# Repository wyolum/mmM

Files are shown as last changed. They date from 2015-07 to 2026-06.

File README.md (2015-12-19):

# mmMercury
mmMercury is an Open Hardware, blood pressure measurement device (not FDA approved).
=======

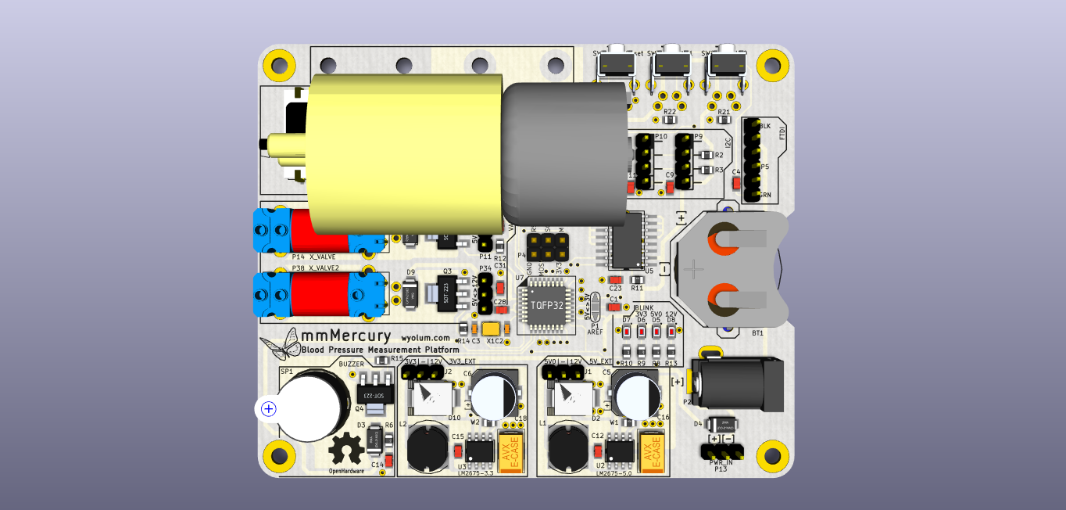
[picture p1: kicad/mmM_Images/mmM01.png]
mmMercury top


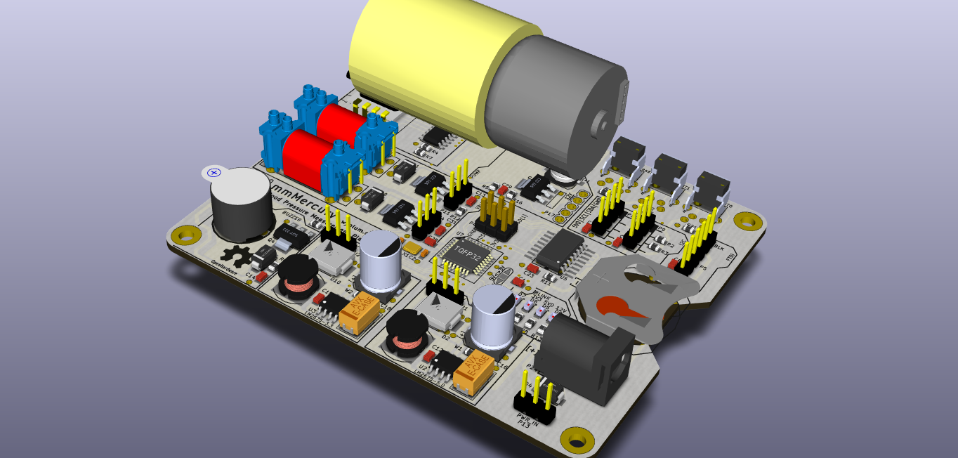
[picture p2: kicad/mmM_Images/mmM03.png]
mmMercury ortho


License
-------
[CERN Open Hardware Licence v1.2 ]

[CERN Open Hardware Licence v1.2 ]:http://www.ohwr.org/attachments/2388/cern_ohl_v_1_2.txt

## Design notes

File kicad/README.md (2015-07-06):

# uCm
uCmini is a laboratory, Open Hardware, blood pressure measurement device (not FDA approved).
Along with the hardware, we will develop an Android app to do the compute BP from the streaming raw data from uCm.  The app will store your BP history, and plot the history. The desire is to get the Open communities involved in the the algorithm development. If we use the Bluefruit Ez-link, the same hardware will work with an FTDI cable.

License
-------
[CERN Open Hardware Licence v1.2 ]

[CERN Open Hardware Licence v1.2 ]:http://www.ohwr.org/attachments/2388/cern_ohl_v_1_2.txt

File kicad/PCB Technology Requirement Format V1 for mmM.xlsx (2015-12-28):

深圳矽递科技有限公司Seeed Technology Inc.
PCB Technology Requirement Format
PCB Name & Version | mmMercury, rev 1
PCB Material PCB板材： | (Rigid)FR－4
PCB Size PCB大小： | mm | ( 99 ) × ( 80 )
PCB Layer PCB层数： | 2
Thickness PCB厚度：
 |  | 1.6mm
Copper Weight铜厚： | 1oz
PCB Colour阻焊颜色： |  | White白色
Silkscreen字符颜色： |  | Black黑色
Pads Finished焊盘喷镀： | (Hasl-lead free)无铅喷锡
Via solder mask阻焊覆盖： |  | solder mask opening过孔开窗
Minimum trace/space (mm)最小线宽 | 0.178mm | Minimum hole size (mm)最小孔径 | 0.508mm
Special requirements特殊工艺： | No | (Put requirements here)
Comment:

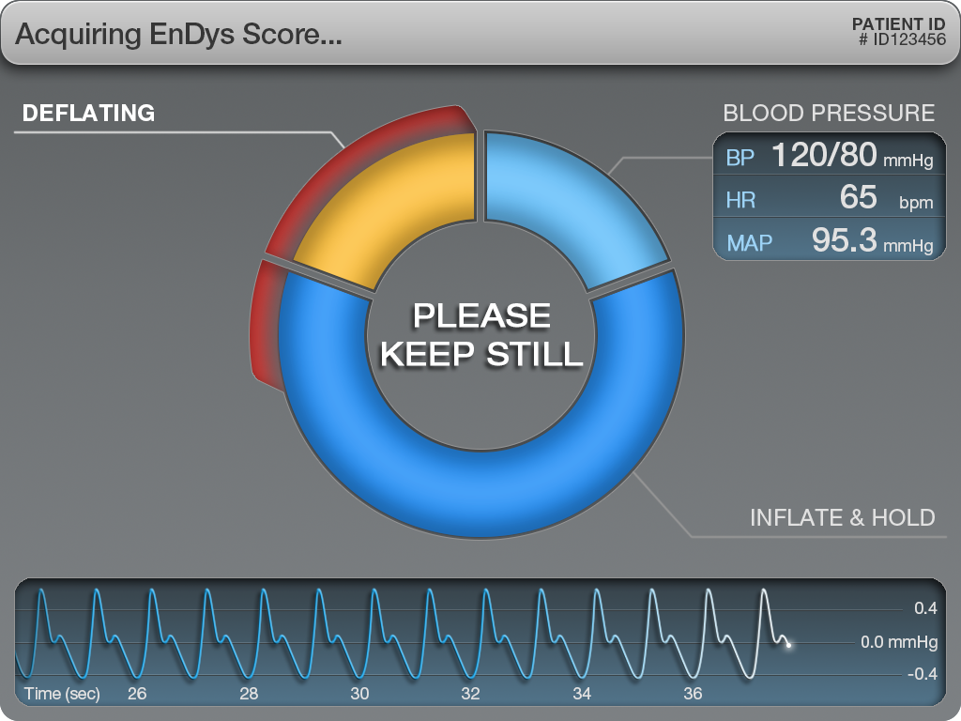
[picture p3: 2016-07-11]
scripts/control_panel/images/4_deflating complete.png

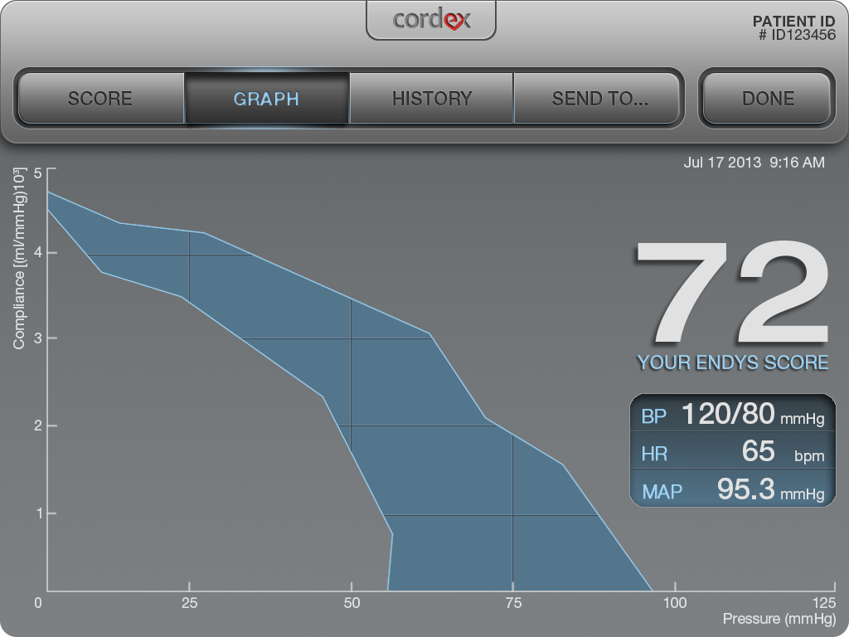
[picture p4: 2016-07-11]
scripts/control_panel/images/6_graph.png

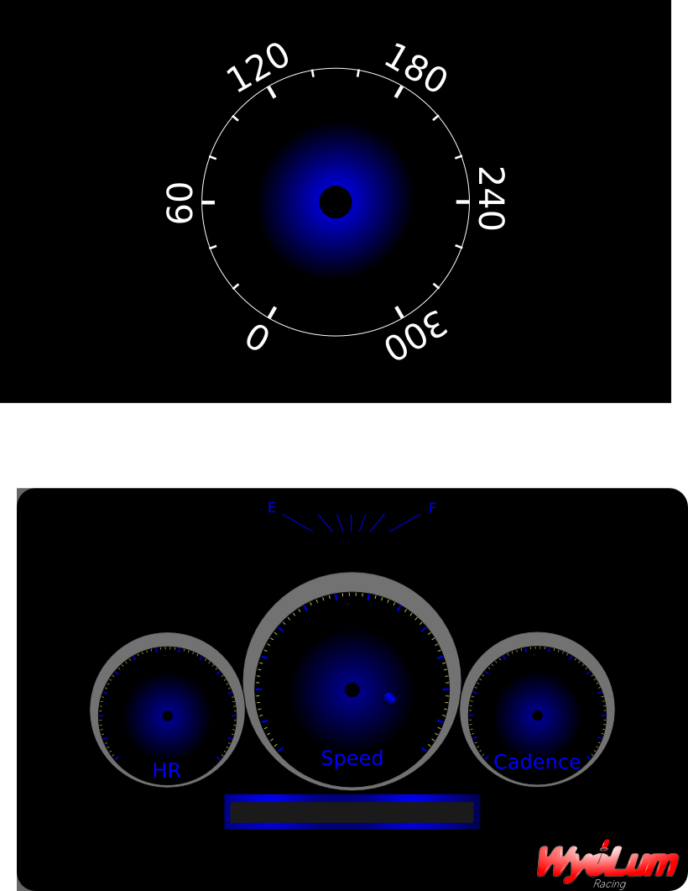
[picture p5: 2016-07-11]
scripts/control_panel/images/background.png

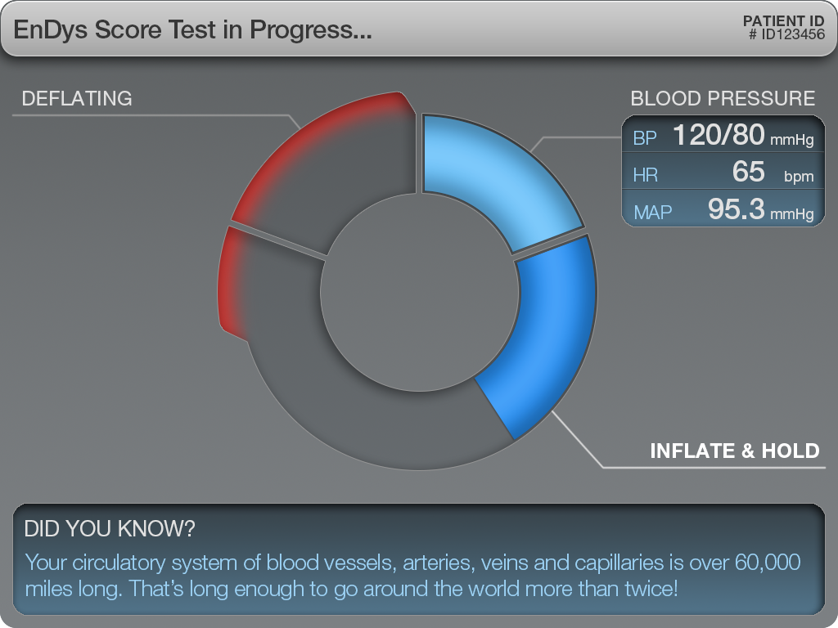
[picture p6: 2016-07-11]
scripts/control_panel/images/2_inflate&hold.png

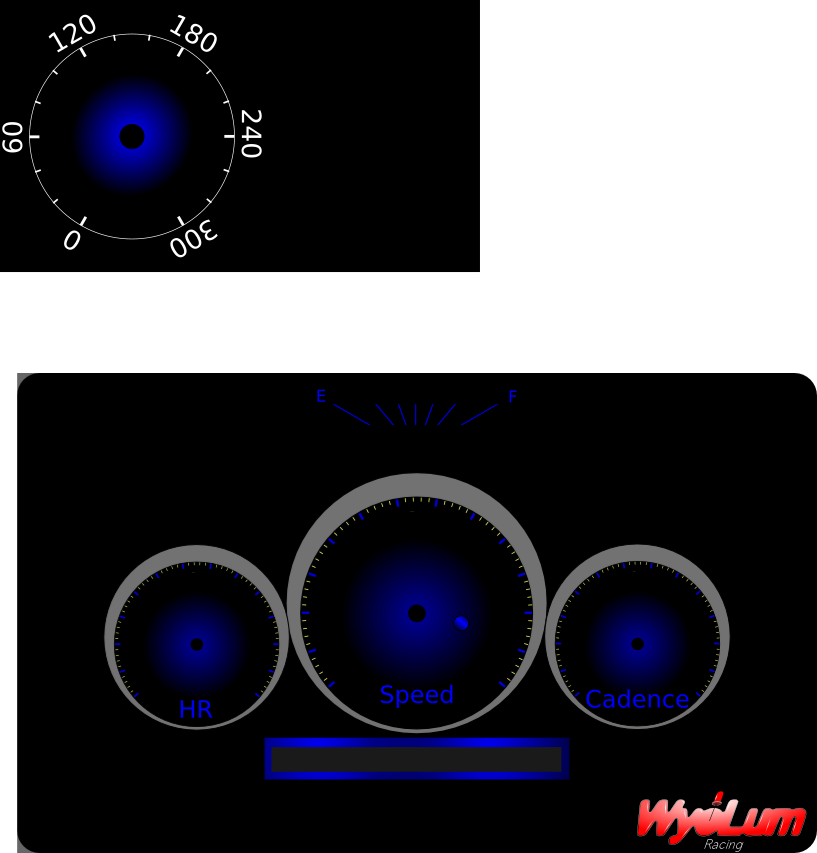
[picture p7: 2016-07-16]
scripts/control_panel/images/background_480_272.png

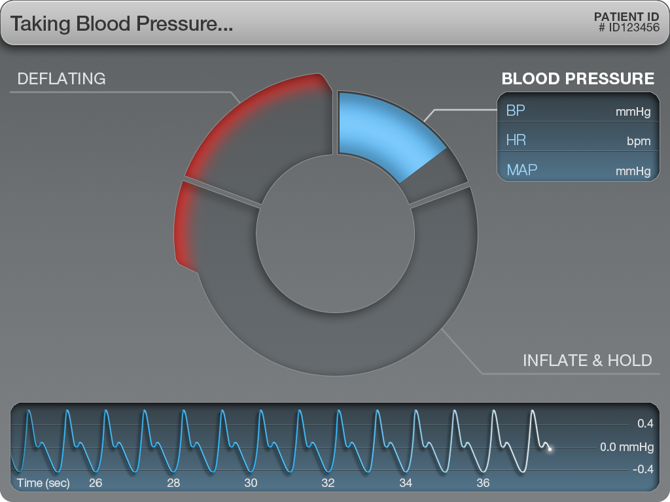
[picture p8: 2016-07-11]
scripts/control_panel/images/1_blood pressure.png

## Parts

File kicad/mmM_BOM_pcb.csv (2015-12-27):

Id | Designator | Package | Quantity | Designation | Supplier and ref
1 | REF62,REF61,REF60,REF1,REF2,REF3,REF4,REF5,REF6,REF7,REF8,REF9,REF10,REF11,REF12,REF13,REF14,REF15,REF16,REF17,REF18,REF19,REF20,REF21,REF22,REF23,REF24,REF25,REF26,REF27,REF55,REF56,REF57,REF58 | via01 | 34 | via01
2 | REF59,REF28,REF29,REF30,REF31,REF32,REF33,REF34,REF35,REF36,REF37,REF38,REF39,REF40,REF41,REF42,REF43,REF44,REF45,REF46,REF47,REF48,REF49,REF50,REF51,REF52,REF53,REF54 | via_th | 28 | via01
3 | B7,B9 | I_O | 2 | PC1
4 | B1,B2,B3 | I_O | 3 | I_O
5 | B4,B12 | I_O | 2 | PB0
6 | B8 | I_O | 1 | PC0
7 | B10 | I_O | 1 | PC6
8 | B11 | I_O | 1 | PC7
9 | BT1 | CR2032 | 1 | BATT_HOLDER
10 | D1,D3,D4,D9 | diode-DO214AC | 4 | ES1D-13-F
11 | D5 | led_0805 | 1 | 5V0
12 | D6 | led_0805 | 1 | 3V3
13 | D7 | led_0805 | 1 | BLINK
14 | D8 | led_0805 | 1 | 12V
15 | P1 | ShortLink2 | 1 | AREF
16 | P4 | Header_ISP | 1 | ICSP
17 | P5 | Header_FTDI | 1 | FTDI
18 | P9,P10 | pin_strip_4-90 | 2 | C3SB
19 | P11 | Header_3 | 1 | VSel_Vlv
20 | P13 | Header_2 | 1 | PWR_IN
21 | P14 | X_Valve_2 | 1 | X_VALVE
22 | P24 | JACK_ALIM | 1 | PWR_IN
23 | P34 | Header_3 | 1 | VSel_Vlv2
24 | P38 | X_Valve_2 | 1 | X_VALVE2
25 | Q1,Q2,Q3,Q4 | SOT223 | 4 | BCP5416TA
26 | SC6,SC7,SC9,SC10 | vite_3mm | 4 | SCREW
27 | SP1 | Speaker | 1 | BUZZER
28 | SW1 | SW_PB_V_H | 1 | Reset
29 | SW2 | SW_PB_V_H | 1 | INT0
30 | SW3 | SW_PB_V_H | 1 | INT1
31 | U5 | DS3231 | 1 | DS3231N
32 | U7 | TQFP32 | 1 | ATMEGA328P-AU-ND
33 | X1 | Xtal_SMD3 | 1 | 16MHz
34 | G1,G2 | Logo-WL3 | 2 | Logo_Wyolum
35 | G3,G4 | OSHW_6mm | 2 | Logo_OH
36 | R22,R21,R11,R4,R3,R2,R1,R12,R14,R15,R16 | r_0805 | 11 | 10k
37 | R13,R10,R6 | r_0805 | 3 | 1k
38 | R9 | r_0805 | 1 | 120E
39 | R8 | r_0805 | 1 | 330E
40 | R5 | r_0805 | 1 | 4k7
41 | C3,C2 | c_0603 | 2 | 22pF
42 | P17 | Pump_P54E01R_03 | 1 | PUMP
43 | W1,W2 | r_0805 | 2 | EN
44 | U3 | SO8E | 1 | LM2675-3.3
45 | U2 | SO8E | 1 | LM2675-5.0
46 | C15,C12 | c_0805 | 2 | 10nF
47 | C1,C4,C7,C8,C9,C10,C11,C13,C14,C17,C23,C28,C29,C31,C19 | c_0805 | 15 | 100nF
48 | C18,C16 | C_2917_HandSoldering | 2 | 100uF 10V
49 | J1 | Header_3 | 1 | 5V_EXT
50 | J2 | Header_3 | 1 | 3V3_EXT
51 | C6,C5 | C_ELCO_SMD_8x10 | 2 | 330uF 25V
52 | L2,L1 | Choke_SMD_Wuerth-784775133 | 2 | 33uH
53 | R7 | r_0805 | 1 | Zero
54 | U1 | TXB0104D | 1 | TXB0104D
55 | D10,D2 | DO-214AB | 2 | SS35
56 | C27 | C_ELCO_SMD | 1 | 100uF
57 | P7 | HCEM500GUH9P3 | 1 | GAGE_PR

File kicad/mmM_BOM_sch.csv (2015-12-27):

Reference | Value | Footprint | Datasheet | manf#
P4 | ICSP | mmM:Header_ISP |  | PREC003DAAN-RC
P1 | AREF | mmM:ShortLink2
SW1 | Reset | mmM:SW_PB_V_H |  | FSMRA3JH
X1 | 16MHz | mmM:Xtal_SMD3 |  | TSX-3225 16.0000MF09Z-AC3
R3 | 10k | mmM:r_0805 |  | RMCF0805JT10K0
R2 | 10k | mmM:r_0805 |  | RMCF0805JT10K0
R1 | 10k | mmM:r_0805 |  | RMCF0805JT10K0
C3 | 22pF | mmM:c_0603 |  | CL10C220JB8NNNC
C2 | 22pF | mmM:c_0603 |  | CL10C220JB8NNNC
P5 | FTDI | mmM:Header_FTDI |  | PREC006SAAN-RC
U7 | ATMEGA328P-AU-ND | mmM:TQFP32 |  | ATMEGA328-AU
B8 | PC0 | mmM:I_O
B9 | PC1 | mmM:I_O
B10 | PC6 | mmM:I_O
B11 | PC7 | mmM:I_O
B12 | PB0 | mmM:I_O
SW2 | INT0 | mmM:SW_PB_V_H |  | FSMRA3JH
SW3 | INT1 | mmM:SW_PB_V_H |  | FSMRA3JH
R22 | 10k | mmM:r_0805 |  | RMCF0805JT10K0
R21 | 10k | mmM:r_0805 |  | RMCF0805JT10K0
C28 | 100nF | mmM:c_0805 |  | CL21B104KCC5PNC
B4 | PB0 | mmM:I_O
SC6 | SCREW | mmM:vite_3mm
SC9 | SCREW | mmM:vite_3mm
SC7 | SCREW | mmM:vite_3mm
SC10 | SCREW | mmM:vite_3mm
B7 | PC1 | mmM:I_O
C1 | 100nF | mmM:c_0805 |  | CL21B104KCC5PNC
C4 | 100nF | mmM:c_0805 |  | CL21B104KCC5PNC
C19 | 100nF | mmM:c_0805 |  | CL21B104KCC5PNC
M1 | OSHW-LOGO | OSHW-LOGO
C27 | 100uF | mmM:C_ELCO_SMD_6x8 |  | UWT1V101MCL1GS
P9 | C3SB | mmM:pin_strip_4-90 |  | PREC004SAAN-RC
U1 | TXB0104D | mmM:TXB0104D |  | TXB0104DR
R4 | 10k | mmM:r_0805 |  | RMCF0805JT10K0
Q1 | BCP5416TA | mmM:SOT223 |  | BCP5416TA
P14 | X_VALVE | mmM:X_Valve_2 |  | X-1-05-S-F
P7 | GAGE_PR | mmM:HCEM500GUH9P3 |  | HCEM500GUH9P3
D1 | ES1D-13-F | mmM:Diode-SMA |  | ES1D-13-F
C17 | 100nF | mmM:c_0805 |  | CL21B104KCC5PNC
C13 | 100nF | mmM:c_0805 |  | CL21B104KCC5PNC
C11 | 100nF | mmM:c_0805 |  | CL21B104KCC5PNC
C10 | 100nF | mmM:c_0805 |  | CL21B104KCC5PNC
C9 | 100nF | mmM:c_0805 |  | CL21B104KCC5PNC
C8 | 100nF | mmM:c_0805 |  | CL21B104KCC5PNC
C7 | 100nF | mmM:c_0805 |  | CL21B104KCC5PNC
P10 | C3SB | mmM:pin_strip_4-90 |  | PREC004SAAN-RC
P11 | VSel_Vlv | mmM:Header_3 |  | PREC003SAAN-RC
Q2 | BCP5416TA | mmM:SOT223 |  | BCP5416TA
P18 | Pump_Cable
R5 | 4k7 | mmM:r_0805 |  | RMCF0805JT4K70
C29 | 100nF | mmM:c_0805 |  | CL21B104KCC5PNC
Q3 | BCP5416TA | mmM:SOT223 |  | BCP5416TA
P38 | X_VALVE2 | mmM:X_Valve_2 |  | X-1-05-S-F
D9 | ES1D-13-F | mmM:Diode-SMA |  | ES1D-13-F
C31 | 100nF | mmM:c_0805 |  | CL21B104KCC5PNC
P34 | VSel_Vlv2 | mmM:Header_3 |  | PREC003SAAN-RC
C14 | 100nF | mmM:c_0805 |  | CL21B104KCC5PNC
Q4 | BCP5416TA | mmM:SOT223 |  | BCP5416TA
D3 | ES1D-13-F | mmM:Diode-SMA |  | ES1D-13-F
R6 | 1k | mmM:r_0805 |  | RMCF0805JT1K00
SP1 | BUZZER | mmM:Speaker |  | PS1240P02BT
P17 | PUMP | mmM:Pump_P54E01R_02 |  | P54E01R
R7 | Zero | mmM:r_0805 |  | RMCF0805ZT0R00
R16 | 10k | mmM:r_0805 |  | RMCF0805JT10K0
R15 | 10k | mmM:r_0805 |  | RMCF0805JT10K0
R12 | 10k | mmM:r_0805 |  | RMCF0805JT10K0
R14 | 10k | mmM:r_0805 |  | RMCF0805JT10K0
R10 | 1k | mmM:r_0805 |  | RMCF0805JT1K00
R13 | 1k | mmM:r_0805 |  | RMCF0805JT1K00
R9 | 120E | mmM:r_0805 |  | RMCF0805JT120R
R8 | 330E | mmM:r_0805 |  | RMCF0805JT330R
P24 | PWR_IN | mmM:JACK_ALIM |  | PJ-002B
D7 | BLINK | mmM:led_0805 |  | LG M67K-H1J2-24-Z
D8 | 12V | mmM:led_0805 |  | LG M67K-H1J2-24-Z
D6 | 3V3 | mmM:led_0805 |  | LG M67K-H1J2-24-Z
D5 | 5V0 | mmM:led_0805 |  | LG M67K-H1J2-24-Z
D4 | ES1D-13-F | mmM:Diode-SMA |  | ES1D-13-F
G4 | Logo_OH | mmM:OSHW_6mm
G3 | Logo_OH | mmM:OSHW_6mm
G2 | Logo_Wyolum | mmM:Logo-WL3
G1 | Logo_Wyolum | mmM:Logo-WL3
P13 | PWR_IN | mmM:Header_2 |  | PRPC002SFAN-RC
U2 | LM2675-5.0 | mmM:SO8E |  | LM2675MX-5.0/NOPB
C16 | 100uF 10V | mmM:C_2917_HandSoldering |  | TPSD107M010R0050
C12 | 10nF | mmM:c_0805 |  | CL21B103KBANNNC
D2 | SS35 | mmM:DO-214AB |  | SS35
W1 | EN | mmM:r_0805
U3 | LM2675-3.3 | mmM:SO8E |  | LM2675MX-3.3/NOPB
C6 | 330uF 25V | mmM:C_ELCO_SMD_8x10 |  | UCL1E331MNL1GS
L2 | 33uH | mmM:Choke_SMD_Wuerth-784775133 |  | 784775133
C15 | 10nF | mmM:c_0805 |  | CL21B103KBANNNC
D10 | SS35 | mmM:DO-214AB |  | SS35
W2 | EN | mmM:r_0805
C18 | 100uF 10V | mmM:C_2917_HandSoldering |  | TPSD107M010R0050
L1 | 33uH | mmM:Choke_SMD_Wuerth-784775133 |  | 784775133
C5 | 330uF 25V | mmM:C_ELCO_SMD_8x10 |  | UCL1E331MNL1GS
J2 | 3V3_EXT | mmM:Header_3 |  | PREC003SAAN-RC
J1 | 5V_EXT | mmM:Header_3 |  | PREC003SAAN-RC
U5 | DS3231N | mmM:DS3231 |  | DS3231S#
R11 | 10k | mmM:r_0805 |  | RMCF0805JT10K0
C23 | 100nF | mmM:c_0805 |  | CL21B104KCC5PNC
BT2 | BATT_COIN |  |  | CR2032
BT1 | BATT_HOLDER | mmM:CR2032 |  | 3003
B3 | I_O | mmM:I_O
B2 | I_O | mmM:I_O
B1 | I_O | mmM:I_O

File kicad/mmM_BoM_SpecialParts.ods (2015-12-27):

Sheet: uCv1_BOM
Reference | Quantity | Description | value | footprint | Manufacturer | Manufacturer PN | Distributor (Link) | Distributor PN
CUSTOM PARTS
P14 | 1 | Miniature Pneumatic Solenoid Valve | X_VALVE | 8mm Solenoid Valve | Parker Hannifin | X-1-05-S-F | Parker Hannifin (http://ph.parker.com/webapp/wcs/stores/servlet/Product2_10151_12051_12163_-1_14107_14097___ProductDisplay) | X-1-05-S-F
P38 | 1 | Miniature Pneumatic Solenoid Valve | X_Valve2 | 8mm Solenoid Valve | Parker Hannifin | X-1-05-S-F | Parker Hannifin (http://ph.parker.com/webapp/wcs/stores/servlet/Product2_10151_12051_12163_-1_14107_14097___ProductDisplay) | X-1-05-S-F
P17 | 1 | Pump_P54E01R_02 | PUMP | custom | Oken Seiko | P54E01R | Oken Seiko (http://www.okenseiko.com/ja/prod/rollingP/air/P54E01R.pdf) | P54E01R
P18 | 1 | Pump Cable | Pump Cable | --
P7 | 1 | Miniature amplified pressure sensor, 3V | GAGE_PR | HCEM500GUH9P3 | SensorTechnics | HCEM500GUH9P3 | SensorTechnics (http://www.sensortechnics.com/en/products/pressure-sensors-and-transmitters/amplified-pressure-sensors/hce/) | HCEM500GUH9P3
P7 | 1 | Miniature amplified pressure sensor, 5V | GAGE_PR | HCEM500GUH9P3 | SensorTechnics | HCEM500GUH9P5 | SensorTechnics (http://www.sensortechnics.com/en/products/pressure-sensors-and-transmitters/amplified-pressure-sensors/hce/) | HCEM500GUH9P5

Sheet: uCv3_sch_BOM
Reference | Value | Footprint | manf#
B1 | I_O | mmM:I_O
B2 | I_O | mmM:I_O
B3 | I_O | mmM:I_O
B4 | PB0 | mmM:I_O
B7 | PC1 | mmM:I_O
B8 | PC0 | mmM:I_O
B9 | PC1 | mmM:I_O
B10 | PC6 | mmM:I_O
B11 | PC7 | mmM:I_O
B12 | PB0 | mmM:I_O
BT1 | BATT_HOLDER | mmM:CR2032 | 3003
BT2 | BATT_COIN |  | CR2032
C1,C4,C7,C8,C9,C10,C11,C13,C14,C17,C23,C28,C29,C31 | 100n | mmM:c_0805 | CL21B104KCC5PNC
C2, C3 | 22pF | mmM:c_0603 | CL10C220JB8NNNC
C3 | 22pF | mmM:c_0603 | CL10C220JB8NNNC
C4 | 100n | mmM:c_0805 | CL21B104KCC5PNC
C5,C6 | 330uF 25V | mmM:C_ELCO_SMD_8x10 | UCL1E331MNL1GS
C6 | 330uF 25V | mmM:C_ELCO_SMD_8x10 | UCL1E331MNL1GS
C7 | 100nF | mmM:c_0805 | CL21B104KCC5PNC
C8 | 100nF | mmM:c_0805 | CL21B104KCC5PNC
C9 | 100nF | mmM:c_0805 | CL21B104KCC5PNC
C10 | 100nF | mmM:c_0805 | CL21B104KCC5PNC
C11 | 100nF | mmM:c_0805 | CL21B104KCC5PNC
C12,C15 | 10nF | mmM:c_0805 | CL21B103KBANNNC
C13 | 100nF | mmM:c_0805 | CL21B104KCC5PNC
C14 | 100nF | mmM:c_0805 | CL21B104KCC5PNC
C15 | 10nF | mmM:c_0805 | CL21B103KBANNNC
C16,C18 | 100uF 10V | mmM:C_2917_HandSoldering | TPSD107M010R0050
C17 | 100nF | mmM:c_0805 | CL21B104KCC5PNC
C18 | 100uF 10V | mmM:C_2917_HandSoldering | TPSD107M010R0050
C23 | 100nF | mmM:c_0805 | CL21B104KCC5PNC
C27 | 100uF | mmM:C_ELCO_SMD_6x8 | UWT1V101MCL1GS
C28 | 100nF | mmM:c_0805 | CL21B104KCC5PNC
C29 | 100nF | mmM:c_0805 | CL21B104KCC5PNC
C31 | 100nF | mmM:c_0805 | CL21B104KCC5PNC
D1,D3,D4,D9 | ES1D-13-F | mmM:Diode-SMA | ES1D-13-F
D2,D10 | SS35 | mmM:DO-214AB | SS35
D3 | ES1D-13-F | mmM:Diode-SMA | ES1D-13-F
D4 | ES1D-13-F | mmM:Diode-SMA | ES1D-13-F
D5,D6,D7,D8 | 5V0 | mmM:led_0805 | LG M67K-H1J2-24-Z
D6 | 3V3 | mmM:led_0805 | LG M67K-H1J2-24-Z
D7 | BLINK | mmM:led_0805 | LG M67K-H1J2-24-Z
D8 | 12V | mmM:led_0805 | LG M67K-H1J2-24-Z
D9 | ES1D-13-F | mmM:Diode-SMA | ES1D-13-F
D10 | SS35 | mmM:DO-214AB | SS35
G1 | Logo_Wyolum | mmM:Logo-WL3
G2 | Logo_Wyolum | mmM:Logo-WL3
G3 | Logo_OH | mmM:OSHW_6mm
G4 | Logo_OH | mmM:OSHW_6mm
J1,J2 | 5V_EXT | mmM:Header_3 | PREC003SAAN-RC
J2 | 3V3_EXT | mmM:Header_3 | PREC003SAAN-RC
L1,L2 | 33uH | mmM:Choke_SMD_Wuerth-784775133 | 784775133
L2 | 33uH | mmM:Choke_SMD_Wuerth-784775133 | 784775133
P1 | AREF | mmM:ShortLink2
P4 | ICSP | mmM:Header_ISP | PREC003DAAN-RC
P5 | FTDI | mmM:Header_FTDI | PREC006SAAN-RC
P7 | GAGE_PR | mmM:HCEM500GUH9P3 | HCEM500GUH9P3
P9,P10 | C3SB | mmM:pin_strip_4-90 | PREC004SAAN-RC
P10 | C3SB | mmM:pin_strip_4-90 | PREC004SAAN-RC
P11,P34 | VSel_Vlv | mmM:Header_3 | PREC003SAAN-RC
P13 | PWR_IN | mmM:Header_2 | PRPC002SFAN-RC
P14,P38 | X_VALVE | mmM:X_Valve_2 | X-1-05-S-F
P17 | PUMP | mmM:Pump_P54E01R_02 | P54E01R
P18 | Pump_Cable
P24 | PWR_IN | mmM:JACK_ALIM | PJ-002B
P34 | VSel_Vlv2 | mmM:Header_3 | PREC003SAAN-RC
P38 | X_VALVE2 | mmM:X_Valve_2 | X-1-05-S-F
Q1,Q2,Q3,Q4 | BCP5416TA | mmM:SOT223 | BCP5416TA
Q2 | BCP5416TA | mmM:SOT223 | BCP5416TA
Q3 | BCP5416TA | mmM:SOT223 | BCP5416TA
Q4 | BCP5416TA | mmM:SOT223 | BCP5416TA
R1R2,R3,R4,R11,R21,R22 | 10k | mmM:r_0805 | RMCF0805JT10K0
R2 | 10k | mmM:r_0805 | RMCF0805JT10K0
R3 | 10k | mmM:r_0805 | RMCF0805JT10K0
R4 | 10k | mmM:r_0805 | RMCF0805JT10K0
R5 | 4k7 | mmM:r_0805 | RMCF0805JT4K70
R6,R10,R13 | 1k | mmM:r_0805 | RMCF0805JT1K00
R7 | Zero | mmM:r_0805 | RMCF0805ZT0R00
R8 | 330E | mmM:r_0805 | RMCF0805JT330R
R9 | 120E | mmM:r_0805 | RMCF0805JT120R
R10 | 1k | mmM:r_0805 | RMCF0805JT1K00
R11 | 10k | mmM:r_0805 | RMCF0805JT10K0
R13 | 1k | mmM:r_0805 | RMCF0805JT1K00
R21 | 10k | mmM:r_0805 | RMCF0805JT10K0
R22 | 10k | mmM:r_0805 | RMCF0805JT10K0
SC6 | SCREW | mmM:vite_3mm
SC7 | SCREW | mmM:vite_3mm
SC9 | SCREW | mmM:vite_3mm
SC10 | SCREW | mmM:vite_3mm
SP1 | BUZZER | mmM:Speaker | PS1240P02BT
SW1,SW2,SW3 | Reset | mmM:SW_PB_V_H | FSMRA3JH
SW2 | INT0 | mmM:SW_PB_V_H | FSMRA3JH
SW3 | INT1 | mmM:SW_PB_V_H | FSMRA3JH
U1 | TXB0104D | mmM:TXB0104D_null | TXB0104DR
U2 | LM2675-5.0 | mmM:SO8E | LM2675MX-5.0/NOPB
U3 | LM2675-3.3 | mmM:SO8E | LM2675MX-3.3/NOPB
U5 | DS3231N | mmM:DS3231 | DS3231S#
U7 | ATMEGA328P-AU-ND | mmM:TQFP32 | ATMEGA328P-AU
W1 | EN | mmM:r_0805
W2 | EN | mmM:r_0805
X1 | 16MHz | mmM:Xtal_SMD3 | TSX-3225 16.0000MF09Z-AC3

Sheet: uCv3_pcb_BOM
Designator | Package | Quantity | Designation
B1,B2,B3 | I_O | 3 | I_O
B4,B12 | I_O | 2 | PB0
B7,B9 | I_O | 2 | PC1
B8 | I_O | 1 | PC0
B10 | I_O | 1 | PC6
B11 | I_O | 1 | PC7
BT1 | CR2032 | 1 | BATT_HOLDER
C1,C4 | c_0805 | 2 | 100n
C3,C2 | c_0603 | 2 | 22pF
C6,C5 | C_ELCO_SMD_8x10 | 2 | 330uF 25V
C1,C4,C7,C8,C9,C10,C11,C13,C14,C17,C23,C28,C29,C31 | c_0805 | 14 | 100nF
C12,C15 | c_0805 | 2 | 10nF
C16,C18 | C_2917_HandSoldering | 2 | 100uF 10V
C27 | C_ELCO_SMD | 1 | 100uF
D1,D3,D4,D9 | diode-DO214AC | 4 | ES1D-13-F
D2,D10 | DO-214AB | 2 | SS35
D5 | led_0805 | 1 | 5V0
D6 | led_0805 | 1 | 3V3
D7 | led_0805 | 1 | BLINK
D8 | led_0805 | 1 | 12V
G1,G2 | Logo-WL3 | 2 | Logo_Wyolum
G3,G4 | OSHW_6mm | 2 | Logo_OH
J1 | Header_3 | 1 | 5V_EXT
J2 | Header_3 | 1 | 3V3_EXT
L1,L2 | Choke_SMD_Wuerth-784775133 | 2 | 33uH
P1 | ShortLink2 | 1 | AREF
P4 | Header_ISP | 1 | ICSP
P5 | Header_FTDI | 1 | FTDI
P7 | HCEM500GUH9P3 | 1 | GAGE_PR
P9,P10 | pin_strip_4-90 | 2 | C3SB
P11 | Header_3 | 1 | VSel_Vlv
P13 | Header_2 | 1 | PWR_IN
P14 | X_Valve_2 | 1 | X_VALVE
P17 | Pump_P54E01R_03 | 1 | PUMP
P24 | JACK_ALIM | 1 | PWR_IN
P34 | Header_3 | 1 | VSel_Vlv2
P38 | X_Valve_2 | 1 | X_VALVE2
Q1,Q2,Q3,Q4 | SOT223 | 4 | BCP5416TA
R1,R2,R3,R4,R11,R21,R22 | r_0805 | 7 | 10k
R5 | r_0805 | 1 | 4k7
R6,R10,R13 | r_0805 | 3 | 1k
R7 | r_0805 | 1 | Zero
R8 | r_0805 | 1 | 330E
R9 | r_0805 | 1 | 120E
REF**,REF**,REF**,REF**,REF**,REF**,REF**,REF**,REF**,REF**,REF**,REF**,REF**,REF**,REF**,REF**,REF**,REF**,REF**,REF**,REF**,REF**,REF**,REF**,REF**,REF**,REF** | via_th | 27 | via01
REF**,REF**,REF**,REF**,REF**,REF**,REF**,REF**,REF**,REF**,REF**,REF**,REF**,REF**,REF**,REF**,REF**,REF**,REF**,REF**,REF**,REF**,REF**,REF**,REF**,REF**,REF**,REF**,REF**,REF**,REF** | via01 | 31 | via01
SC6,SC7,SC9,SC10 | vite_3mm | 4 | SCREW
SP1 | Speaker | 1 | BUZZER
SW1 | SW_PB_V_H | 1 | Reset
SW2 | SW_PB_V_H | 1 | INT0
SW3 | SW_PB_V_H | 1 | INT1
U1 | TXB0104D_null | 1 | TXB0104D
U2 | SO8E | 1 | LM2675-5.0
U3 | SO8E | 1 | LM2675-3.3
U5 | DS3231 | 1 | DS3231N
U7 | TQFP32 | 1 | ATMEGA328-AU-ND
W1,W2 | r_0805 | 2 | EN
X1 | Xtal_SMD3 | 1 | 16MHz

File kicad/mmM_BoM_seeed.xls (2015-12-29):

Electronic Engineering BOM List
Product Name : mmMercury (Open Source Blood Pressure Measurement platform)
Version：V1.0
Issue Date：28/Dec/2015
Item No. (序号) | Reference Des (上件位置) | Qty (用量) | Catalog (分类） | Part_Description (规格描述) | Part_Value （元件值） | Part_Package （元件封装） | Manufacturers Name (使用厂牌名称) | Manufacturers Part No. (使用厂牌型号) | Distributors Name （供应商名称） | Distributors Part No. (供貨商型号) | Unit Price （单价） | Price Break To Use （价格分段的购买量） | Notes/Remark （备注）
Example（填写范例）
1 | BT1 | 1 | OTHER | HOLDER BATTERY COIN 20MM DIA THM | BATT_HOLDER | CR2032 | Keystone Electronics | 3003 | Digikey (http://www.digikey.com/scripts/DkSearch/dksus.dll?x=0&y=0&lang=en&KeyWords=3003K-ND&cur=USD) | 3003K-ND
2 | BT2 | 1 | OTHER | BATTERY LITHIUM COIN 3V 20MM | BATT_COIN | -- | Panasonic - BSG | CR2032 | Digikey (http://www.digikey.com/product-detail/en/CR2032/P189-ND/31939?cur=USD) | P189-ND
3 | C1,C4,C7,C8,C9,C10,C11,C13,C14,C17,C23,C28,C29,C31 | 14 | Capacitor | CAP CER 0.1UF 100V 10% X7R 0805 | 100nF, 100V | 0805 (2012 Metric) | Samsung Electro-Mechanics America, Inc | CL21B104KCC5PNC | Digikey (http://www.digikey.com/product-detail/en/CL21B104KCC5PNC/1276-2447-1-ND/3890533) | 1276-2447-1-ND
4 | C2, C3 | 2 | Capacitor | CAP CER 22PF 50V 5% NP0 0603 | 22pF, 50V | 0603 (1608 Metric) | Samsung Electro-Mechanics America, Inc | CL10C220JB8NNNC | Digikey (http://www.digikey.com/product-detail/en/CL10C220JB8NNNC/1276-1023-1-ND/3889109) | 1276-1023-1-ND
5 | C5,C6 | 2 | Capacitor | CAP ALUM 330UF 20% 25V SMD | 330uF 25V | Radial, Can – SMD, 8mm x 10mm | Nichicon | UCL1E331MNL1GS | Digikey (http://www.digikey.com/product-detail/en/UCL1E331MNL1GS/493-3943-1-ND/2300370) | 493-3943-1-ND
6 | C12,C15 | 2 | Capacitor | CAP CER 10000PF 50V X7R 0805 | 10nF | 0805 (2012 Metric) | Samsung Electro-Mechanics America, Inc | CL21B103KBANNNC | Digikey (http://www.digikey.com/product-detail/en/CL21B103KBANNNC/1276-1015-1-ND/3889101) | 1276-1015-1-ND
7 | C16,C18 | 2 | Capacitor | CAP TANT 100UF 10V 20% 2917 | 100uF 10V | 2917 (7343 Metric) | AVX Corporation | TPSD107M010R0050 | Digikey (http://www.digikey.com/product-detail/en/TPSD107M010R0050/478-4095-1-ND/1164431) | 478-4095-1-ND
8 | C27 | 1 | Capacitor | CAP ALUM 100UF 20% 35V SMD | 100uF | Radial, Can – SMD, 6.3mm x 7.7mm | Nichicon | UWT1V101MCL1GS | Digikey (http://www.digikey.com/product-detail/en/UWT1V101MCL1GS/493-2203-1-ND/590178) | 493-2203-1-ND
9 | D1, D3, D4, D9 | 4 | Diode | DIODE GEN PURP 200V 1A SMA | ES1D-13-F | DO-214AC, SMA | Diodes Inc | ES1D-13-F | Digikey (http://www.digikey.com/product-detail/en/ES1D-13-F/ES1D-FDICT-ND/768882) | ES1D-FDICT-ND
10 | D2,D10 | 2 | Diode | DIODE SCHOTTKY 50V 3A SMC | SS35 | DO-214AB, SMC | Fairchild Semiconductor | SS35 | Digikey (http://www.digikey.com/product-detail/en/SS35/SS35FSCT-ND/3478328) | SS35FSCT-ND
11 | D5 D6 D7 D8 | 4 | Diode | LED MINI TOPLED GREEN 570NM SMD | LED 5V0 LED 3V3 LED BLINK LED 12V | 2-SMD, J-Lead | OSRAM Opto Semiconductors Inc | LG M67K-H1J2-24-Z | Digikey (http://www.digikey.com/product-detail/en/LG%20M67K-H1J2-24-Z/475-2730-1-ND/1938897) | 475-2730-1-ND
12 | L1, L2 | 2 | OTHER | FIXED IND 33UH 1.35A 130 MOHM | 33uH | SMD 0.307" L x 0.276" W (7.80mm x 7.00mm) | Wurth Electronics Inc | 784775133 | Digikey (http://www.digikey.com/product-detail/en/784775133/732-6860-1-ND/5169154) | 732-6860-1-ND
13 | P24 | 1 | Connector | CONN POWER JACK MALE 2.5MM CLSD | PWR_IN | Through Hole, Right Angle, 2.5mm ID, 5.5mm OD | CUI Inc | PJ-002B | DigiKey (http://www.digikey.com/product-search/en?vendor=0&keywords=CP-002B-ND) | CP-002B-ND
14 | Q1, Q2, Q3, Q4 | 4 | Transistor | TRANS NPN 45V 1A 2W SOT223 | BCP5416TA | SOT-223 | Diodes Inc | BCP5416TA | Digikey (http://www.digikey.com/product-detail/en/BCP5416TA/BCP5416TACT-ND/2712056) | BCP5416TACT-ND
15 | R1, R2, R3, R11, R12, R14, R15, R16, R21, R22 | 10 | Resister | RES 10K OHM 1/8W 5% 0805 | 10k | 0805 (2012 Metric) | Stackpole Electronics Inc | RMCF0805JT10K0 | DigiKey (http://www.digikey.com/product-detail/en/RMCF0805JT10K0/RMCF0805JT10K0CT-ND/1942577) | RMCF0805JT10K0CT-ND
16 | R5 | 1 | Resister | RES 4.7K OHM 1/8W 5% 0805 | 4k7 | 0805 (2012 Metric) | Stackpole Electronics Inc | RMCF0805JT4K70 | DigiKey (http://www.digikey.com/product-detail/en/RMCF0805JT4K70/RMCF0805JT4K70CT-ND/1942570) | RMCF0805JT4K70CT-ND
17 | R6, R10, R13 | 3 | Resister | RES 1K OHM 1/8W 5% 0805 | 1k | 0805 (2012 Metric) | Stackpole Electronics Inc | RMCF0805JT1K00 | DigiKey (http://www.digikey.com/product-detail/en/RMCF0805JT1K00/RMCF0805JT1K00CT-ND/1942557) | RMCF0805JT1K00CT-ND
18 | R7 | 1 | Resister | RES SMD 0.0 OHM JUMPER 1/8W 0805 | 0 ohms | 0805 (2012 Metric) | Stackpole Electronics Inc | RMCF0805ZT0R00 | DigiKey (http://www.digikey.com/product-detail/en/RMCF0805ZT0R00/RMCF0805ZT0R00CT-ND/1942606) | RMCF0805ZT0R00CT-ND
19 | R8 | 1 | Resister | RES 330 OHM 1/8W 5% 0805 | 330 | 0805 (2012 Metric) | Stackpole Electronics Inc | RMCF0805JT330R | Digikey (http://www.digikey.com/product-detail/en/RMCF0805JT330R/RMCF0805JT330RCT-ND/1942547) | RMCF0805JT330RCT-ND
20 | R9 | 1 | Resister | RES 120 OHM 1/8W 5% 0805 | 120 | 0805 (2012 Metric) | Stackpole Electronics Inc | RMCF0805JT120R | DigiKey (http://www.digikey.com/product-detail/en/RMCF0805JT120R/RMCF0805JT120RCT-ND/1942540) | RMCF0805JT120RCT-ND
21 | SP1 | 1 | OTHER | BUZZER PIEZO 4KHZ 12.2MM PC MNT | BUZZER | Circular - 12.20mm Dia x 6.50mm H, 5mm pitch | TDK Corporation | PS1240P02BT | DigiKey (http://www.digikey.com/product-detail/en/PS1240P02BT/445-2525-1-ND/935930) | 445-2525-1-ND
22 | SW1 SW2 SW3 | 3 | OTHER | SWITCH TACTILE SPST-NO 0.05A 12V | Reset INT0 INT1 | Through Hole, Right Angle | TE Connectivity | FSMRA3JH | DigiKey (http://www.digikey.com/product-detail/en/FSMRA3JH/450-1657-ND/1632543?cur=USD) | 450-1657-ND
23 | U2 | 1 | IC | IC REG BUCK 5V 1A 8SOIC | LM2675-5.0 | 8-SOIC (0.154", 3.90mm Width) | Texas Instruments | LM2675MX-5.0/NOPB | DigiKey (http://www.digikey.com/product-detail/en/LM2675MX-5.0%2FNOPB/LM2675MX-5.0%2FNOPBCT-ND/3440121) | LM2675MX-5.0/NOPBCT-ND
24 | U3 | 1 | IC | IC REG BUCK 3.3V 1A 8SOIC | LM2675-3.3 | 8-SOIC (0.154", 3.90mm Width) | Texas Instruments | LM2675MX-3.3/NOPB | DigiKey (http://www.digikey.com/product-detail/en/LM2675MX-3.3%2FNOPB/LM2675MX-3.3%2FNOPBCT-ND/3440120) | LM2675MX-3.3/NOPBCT-ND
25 | U5 | 1 | IC | IC RTC W/TCXO 16-SOIC | DS3231S# | 16-SOIC (0.295", 7.50mm Width) | Maxim Integrated | DS3231S# | DigiKey (http://www.digikey.com/product-detail/en/DS3231S) | DS3231S#-ND
26 | U7 | 1 | IC | IC MCU 8BIT 32KB FLASH 32TQFP | ATMEGA328P-AU | 32-TQFP | Atmel | ATMEGA328P-AU | DigiKey (http://www.digikey.com/product-search/en?vendor=0&keywords=ATMEGA328P-AU-ND) | ATMEGA328P-AU-ND
27 | X1 | 1 | OTHER | CRYSTAL 16MHZ 9PF SMD | 16MHz | 4-SMD, No Lead (DFN, LCC) | EPSON | TSX-3225 16.0000MF09Z-AC3 | DigiKey (http://www.digikey.com/product-detail/en/TSX-3225%2016.0000MF09Z-AC3/SER3628CT-ND/1802879) | SER3628CT-ND
 | DO NOT POPULATE – MAKE KIT OF PARTS FOR CONNECTORS
 | HEADERS, 0.1” SINGLE ROW
28 | P13 | 1 | Connector | CONN HEADER .100" SNGL STR 2POS | PWR_IN | Through hole, 0.100" (2.54mm) | Sullins Connector Solutions | PRPC002SFAN-RC | Digikey (http://www.digikey.com/product-detail/en/PRPC002SFAN-RC/S1211EC-02-ND/2775372) | S1211EC-02-ND
29 | J1 J2 P11 P34 | 4 | Connector | CONN HEADER .100" SNGL STR 3POS | 5V_EXT 3V3_EXT Vsel_Vlv Vsel_Vlv2 | Through hole, 0.100" (2.54mm) | Sullins Connector Solutions | PREC003SAAN-RC | Digikey (http://www.digikey.com/product-detail/en/PREC003SAAN-RC/S1012EC-03-ND/2774851) | S1012EC-03-ND
30 | P5 | 1 | Connector | CONN HEADER .100" SNGL STR 6POS | Header_FTDI | Through hole, 0.100" (2.54mm) | Sullins Connector Solutions | PREC006SAAN-RC | Digikey (http://www.digikey.com/product-search/en?vendor=0&keywords=PREC006SAAN-RC) | S1012EC-06-ND
31 | P9,P10 | 2 | Connector | CONN HEADER .100" SNGL STR 4POS | C3SB | Through hole, 0.100" (2.54mm) | Sullins Connector Solutions | PREC004SAAN-RC | Digikey (http://www.digikey.com/product-search/en?vendor=0&keywords=PREC004SAAN-RC) | S1012EC-04-ND
 | HEADERS, 0.1” DOUBLE ROW
32 | P4 | 1 | Connector | CONN HEADER .100" DUAL STR 6POS | Header_ISP | Through hole, 0.100" (2.54mm) | Sullins Connector Solutions | PREC003DAAN-RC | Digikey (http://www.digikey.com/product-detail/en/PREC003DAAN-RC/S2012EC-03-ND/2774891) | S2012EC-03-ND
1. Recommended Distributor: Digi-Key, Mouser, Avnet Express, Farnell.
2. Catalog: Capacitor,Resister,Diode,Connector,Transistor,IC,PROTECTOR CATEGORY,OTHER
3. Required Fields: Item No, Reference Des, Qty, Catalog, Part_Value, Part Package
Optional Fields: Part_Description, Manufacturers Name, Manufacturers Part No, Distributors Name, Distributors Part No, Unit Cost, Price break to use, Notes/Remark

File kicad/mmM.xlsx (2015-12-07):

 |  |  |  |  |  |  | Board Qty: | 1
 |  |  |  |  |  |  | Total Cost: | $38.65 |  |  |  | $31.84 |  |  |  |  |  | $42.34 |  |  |  |  |  | $1081.30
 |  |  |  |  |  |  | Unit Cost: | $38.65
Global Part Info |  |  |  |  |  |  |  |  | Newark |  |  |  |  |  | Digi-Key |  |  |  |  |  | Mouser
Refs | Value | Desc | Footprint | Manf | Manf# | Qty | Unit$ | Ext$ | Avail | Purch | Unit$ | Ext$ | Cat# | Doc | Avail | Purch | Unit$ | Ext$ | Cat# | Doc | Avail | Purch | Unit$ | Ext$ | Cat# | Doc
B1-B3 | I_O |  | uCm:I_O |  |  | 3 | $0.00 | $0.00
B10 | PC6 |  | uCm:I_O |  |  | 1 | $0.00 | $0.00
B11 | PC7 |  | uCm:I_O |  |  | 1 | $0.00 | $0.00
B4,B12 | PB0 |  | uCm:I_O |  |  | 2 | $0.00 | $0.00
B7,B9 | PC1 |  | uCm:I_O |  |  | 2 | $0.00 | $0.00
B8 | PC0 |  | uCm:I_O |  |  | 1 | $0.00 | $0.00
BT1 | BATT_HOLDER |  | uCm:CR2032 |  | 3003 | 1 | $0.38 | $0.38 |  |  |  |  |  |  |  |  |  |  |  |  | 18267 |  | $0.38 | $0.38 | 534-3003 | Link (http://www.mouser.com/ProductDetail/Keystone-Electronics/3003/?qs=sGAEpiMZZMsQtlBhqKq43UjvIYJWuKJP)
BT2 | BATT_COIN |  |  |  | CR2032 | 1 | $0.00 | $0.00 | 4730 |  | $0.73 | $0.73 | 13C1019 | Link (http://www.newark.com/panasonic-batteries/cr2032/lithium-battery-3v-coin-cell/dp/13C1019) |  |  |  |  |  |  |  |  | $0.00 | $0.00 | 658-CR2032 | Link (http://www.mouser.com/ProductDetail/Panasonic-Battery/CR2032/?qs=sGAEpiMZZMtLck3p7ZBovbxA0OP75j3l)
C1,C4 | 100n |  | uCm:c_0805 |  | CL21B104KCC5PNC | 2 | $0.03 | $0.07 | 20000 |  | $0.03 | $0.07 | 87R4068 | Link (http://www.newark.com/tdk/c2012x7r2a104k125aa/ceramic-capacitor-0-1uf-100v-x7r/dp/87R4068) | 505709 |  | $0.11 | $0.22 | 1276-2447-1-ND | Link (http://www.digikey.com/product-detail/en/CL21B104KCC5PNC/1276-2447-1-ND/3890533)
C12,C15 | 10nF |  | uCm:c_0805 |  | CL21B103KBANNNC | 2 | $0.10 | $0.20 | 1958 |  | $0.10 | $0.20 | 06R3733 | Link (http://www.newark.com/multicomp/mc0805b103k500ct/ceramic-capacitor-0-01uf-50v-x7r/dp/06R3733) | 213312 |  | $0.10 | $0.20 | 1276-1015-1-ND | Link (http://www.digikey.com/product-detail/en/CL21B103KBANNNC/1276-1015-1-ND/3889101)
C16,C18 | 100uF 10V |  | uCm:C_2917_HandSoldering |  | TPSD107M010R0050 | 2 | $3.30 | $6.60 | 21 |  | $3.30 | $6.60 | 75M2941 | Link (http://www.newark.com/avx/tpsd107m010r0050/tantalum-capacitor-100uf-10v-0/dp/75M2941) | 1935 |  | $3.49 | $6.98 | 478-4095-1-ND | Link (http://www.digikey.com/product-detail/en/TPSD107M010R0050/478-4095-1-ND/1164431) | 664 |  | $3.43 | $6.86 | 581-TPSD107M010R0050 | Link (http://www.mouser.com/Search/Refine.aspx?Keyword=TPSD107M010R0050)
C2,C3 | 22pF |  | uCm:c_0603 |  | CL10C220JB8NNNC | 2 | $0.10 | $0.20 | 11394 |  | $0.10 | $0.20 | 90R7643 | Link (http://www.newark.com/tdk/c1608c0g1h220j080aa/ceramic-capacitor-22pf-50v-c0g/dp/90R7643) | 97810 |  | $0.10 | $0.20 | 1276-1023-1-ND | Link (http://www.digikey.com/product-detail/en/CL10C220JB8NNNC/1276-1023-1-ND/3889109)
C27 | 100uF |  | uCm:C_ELCO_SMD_6x8 |  | UWT1V101MCL1GS | 1 | $0.35 | $0.35 | 1788 |  | $0.45 | $0.45 | 58R3591 | Link (http://www.newark.com/nichicon/uwt1v101mcl1gs/aluminum-electrolytic-capacitor/dp/58R3591) | 62131 |  | $0.36 | $0.36 | 493-2203-1-ND | Link (http://www.digikey.com/product-detail/en/UWT1V101MCL1GS/493-2203-1-ND/590178) | 9201 |  | $0.35 | $0.35 | 647-UWT1V101MCL1S | Link (http://www.mouser.com/Search/Refine.aspx?Keyword=UWT1V101MCL1GS)
C5,C6 | 330uF 25V |  | uCm:C_ELCO_SMD_8x10 |  | UCL1E331MNL1GS | 2 | $0.93 | $1.87 | 0 |  | $1.06 | $2.12 | 84R9000 | Link (http://www.newark.com/nichicon/ucl1e331mnl1gs/aluminum-electrolytic-capacitor/dp/84R9000) | 16220 |  | $0.95 | $1.90 | 493-3943-1-ND | Link (http://www.digikey.com/product-detail/en/UCL1E331MNL1GS/493-3943-1-ND/2300370) | 4 |  | $0.93 | $1.87 | 647-UCL1E331MNL1GS | Link (http://www.mouser.com/Search/Refine.aspx?Keyword=UCL1E331MNL1GS)
C7-C11,C13,C14,C17,C23,C28,C29,C31 | 100nF |  | uCm:c_0805 |  | CL21B104KCC5PNC | 12 | $0.03 | $0.40 | 20000 |  | $0.03 | $0.40 | 87R4068 | Link (http://www.newark.com/tdk/c2012x7r2a104k125aa/ceramic-capacitor-0-1uf-100v-x7r/dp/87R4068) | 505709 |  | $0.08 | $0.94 | 1276-2447-1-ND | Link (http://www.digikey.com/product-detail/en/CL21B104KCC5PNC/1276-2447-1-ND/3890533)
D1,D3,D4,D9 | ES1D-13-F |  | uCm:Diode-SMA |  | ES1D-13-F | 4 | $0.40 | $1.62 | 8497 |  | $0.40 | $1.62 | 23T5896 | Link (http://www.newark.com/webapp/wcs/stores/servlet/Search?catalogId=15003&langId=-1&storeId=10194&gs=true&st=ES1D-13-F) | 13431 |  | $0.46 | $1.84 | ES1D-FDICT-ND | Link (http://www.digikey.com/product-detail/en/ES1D-13-F/ES1D-FDICT-ND/768882) | 5238 |  | $0.55 | $2.20 | 621-ES1D-F | Link (http://www.mouser.com/Search/Refine.aspx?Keyword=ES1D-13-F)
D2,D10 | SS35 |  | uCm:DO-214AB |  | SS35 | 2 | $0.61 | $1.22 |  |  |  |  |  |  |  |  |  |  |  |  | 4333 |  | $0.61 | $1.22 | 512-SS35 | Link (http://www.mouser.com/ProductDetail/Fairchild-Semiconductor/SS35/?qs=sGAEpiMZZMv%252bkWzvOmGqmmaLmAIVtKWI)
D5 | 5V0 |  | uCm:led_0805 |  | LG M67K-H1J2-24-Z | 1 | $0.20 | $0.20 |  |  |  |  |  |  | 29428 |  | $0.34 | $0.34 | 475-2730-1-ND | Link (http://www.digikey.com/product-detail/en/LG%20M67K-H1J2-24-Z/475-2730-1-ND/1938897) | 19994 |  | $0.20 | $0.20 | 720-LGM67KH1J224Z | Link (http://www.mouser.com/Search/Refine.aspx?Keyword=LG%20M67K-H1J2-24-Z)
D6 | 3V3 |  | uCm:led_0805 |  | LG M67K-H1J2-24-Z | 1 | $0.20 | $0.20 |  |  |  |  |  |  | 29428 |  | $0.34 | $0.34 | 475-2730-1-ND | Link (http://www.digikey.com/product-detail/en/LG%20M67K-H1J2-24-Z/475-2730-1-ND/1938897) | 19994 |  | $0.20 | $0.20 | 720-LGM67KH1J224Z | Link (http://www.mouser.com/Search/Refine.aspx?Keyword=LG%20M67K-H1J2-24-Z)
D7 | BLINK |  | uCm:led_0805 |  | LG M67K-H1J2-24-Z | 1 | $0.20 | $0.20 |  |  |  |  |  |  | 29428 |  | $0.34 | $0.34 | 475-2730-1-ND | Link (http://www.digikey.com/product-detail/en/LG%20M67K-H1J2-24-Z/475-2730-1-ND/1938897) | 19994 |  | $0.20 | $0.20 | 720-LGM67KH1J224Z | Link (http://www.mouser.com/Search/Refine.aspx?Keyword=LG%20M67K-H1J2-24-Z)
D8 | 12V |  | uCm:led_0805 |  | LG M67K-H1J2-24-Z | 1 | $0.20 | $0.20 |  |  |  |  |  |  | 29428 |  | $0.34 | $0.34 | 475-2730-1-ND | Link (http://www.digikey.com/product-detail/en/LG%20M67K-H1J2-24-Z/475-2730-1-ND/1938897) | 19994 |  | $0.20 | $0.20 | 720-LGM67KH1J224Z | Link (http://www.mouser.com/Search/Refine.aspx?Keyword=LG%20M67K-H1J2-24-Z)
G1,G2 | Logo_Wyolum |  | uCm:Logo-WL3 |  |  | 2 | $0.00 | $0.00
G3,G4 | Logo_OH |  | uCm:OSHW_6mm |  |  | 2 | $0.00 | $0.00
J1 | 5V_EXT |  | uCm:Header_2 |  | PRPC002SFAN-RC | 1 | $0.18 | $0.18 |  |  |  |  |  |  | 0 |  | $0.18 | $0.18 | S1211EC-02-ND | Link (http://www.digikey.com/scripts/DkSearch/dksus.dll?WT.z_header=search_go&lang=en)
J2 | 3V3_EXT |  | uCm:Header_2 |  | PRPC002SFAN-RC | 1 | $0.18 | $0.18 |  |  |  |  |  |  | 0 |  | $0.18 | $0.18 | S1211EC-02-ND | Link (http://www.digikey.com/scripts/DkSearch/dksus.dll?WT.z_header=search_go&lang=en)
L1,L2 | 33uH |  | uCm:Ind_Schott_330uH |  | 34595 | 2 | $0.48 | $0.95 | 60 |  | $0.48 | $0.95 | 02N4623 | Link (http://www.newark.com/webapp/wcs/stores/servlet/Search?catalogId=15003&langId=-1&storeId=10194&gs=true&st=34595) |  |  |  |  |  |  | 0 |  | $521.55 | $1043.10 | 571-734595-1 | Link (http://www.mouser.com/ProductDetail/TE-Connectivity/734595-1/?qs=sGAEpiMZZMuDGvNOpmBhkSctutTq8hR5)
P1 | AREF |  | uCm:ShortLink2 |  |  | 1 | $0.00 | $0.00
P11 | VSel_Vlv |  | uCm:Header_3 |  | PREC003SAAN-RC | 1 | $0.14 | $0.14 |  |  |  |  |  |  | 0 |  | $0.14 | $0.14 | S1012EC-03-ND | Link (http://www.digikey.com/scripts/DkSearch/dksus.dll?WT.z_header=search_go&lang=en)
P13 | PWR_IN |  | uCm:Header_2 |  | PRPC002SFAN-RC | 1 | $0.18 | $0.18 |  |  |  |  |  |  | 0 |  | $0.18 | $0.18 | S1211EC-02-ND | Link (http://www.digikey.com/scripts/DkSearch/dksus.dll?WT.z_header=search_go&lang=en)
P14 | X_VALVE |  | uCm:X_Valve_2 |  | X-1-05-S-F | 1 | $0.00 | $0.00
P17 | PUMP |  | uCm:Pump_P54E01R_02 |  | P54E01R | 1 | $0.00 | $0.00
P18 | Pump_Cable |  |  |  |  | 1 | $0.00 | $0.00
P24 | PWR_IN |  | uCm:JACK_ALIM |  | PJ-002B | 1 | $0.91 | $0.91 |  |  |  |  |  |  | 33937 |  | $0.93 | $0.93 | CP-002B-ND | Link (http://www.digikey.com/product-detail/en/PJ-002B/CP-002B-ND/96965) | 8753 |  | $0.91 | $0.91 | 490-PJ-002B | Link (http://www.mouser.com/ProductDetail/CUI/PJ-002B/)
P34 | VSel_Vlv2 |  | uCm:Header_3 |  | PREC003SAAN-RC | 1 | $0.14 | $0.14 |  |  |  |  |  |  | 0 |  | $0.14 | $0.14 | S1012EC-03-ND | Link (http://www.digikey.com/scripts/DkSearch/dksus.dll?WT.z_header=search_go&lang=en)
P38 | X_VALVE2 |  | uCm:X_Valve_2 |  | X-1-05-S-F | 1 | $0.00 | $0.00
P4 | ICSP |  | uCm:Header_ISP |  | PREC003DAAN-RC | 1 | $0.28 | $0.28 |  |  |  |  |  |  | 0 |  | $0.28 | $0.28 | S2012EC-03-ND | Link (http://www.digikey.com/scripts/DkSearch/dksus.dll?WT.z_header=search_go&lang=en)
P5 | FTDI |  | uCm:Header_FTDI |  | PREC006SAAN-RC | 1 | $0.18 | $0.18 |  |  |  |  |  |  | 1 |  | $0.18 | $0.18 | S1012EC-06-ND | Link (http://www.digikey.com/scripts/DkSearch/dksus.dll?WT.z_header=search_go&lang=en)
P7 | GAGE_PR |  | uCm:HCEM500GUH9P3 |  | HCEM500GUH9P3 | 1 | $0.00 | $0.00
P9,P10 | C3SB |  | uCm:pin_strip_4-90 |  | PREC004SAAN-RC | 2 | $0.15 | $0.30 |  |  |  |  |  |  | 0 |  | $0.15 | $0.30 | S1012EC-04-ND | Link (http://www.digikey.com/scripts/DkSearch/dksus.dll?WT.z_header=search_go&lang=en)
Q1-Q4 | BCP5416TA |  | uCm:SOT223 |  | BCP5416TA | 4 | $0.42 | $1.68 |  |  |  |  |  |  | 1016 |  | $0.42 | $1.68 | BCP5416TACT-ND | Link (http://www.digikey.com/product-detail/en/BCP5416TA/BCP5416TACT-ND/2712056) | 0 |  | $0.47 | $1.88 | 522-BCP5416TA | Link (http://www.mouser.com/ProductDetail/Diodes-Incorporated/BCP5416TA/)
R1-R3,R21,R22 | 10k |  | uCm:r_0805 |  | RMCF0805JT10K0 | 5 | $0.003 | $0.01 | 0 |  | $0.003 | $0.01 | 83R8240 | Link (http://www.newark.com/vishay-dale/crcw080510k0jneb/res-thick-film-10k-5-0-125w-0805/dp/83R8240) | 1290794 |  | $0.10 | $0.50 | RMCF0805JT10K0CT-ND | Link (http://www.digikey.com/product-detail/en/RMCF0805JT10K0/RMCF0805JT10K0CT-ND/1942577)
R10,R13 | 1k |  | uCm:r_0805 |  | RMCF0805JT1K00 | 2 | $0.08 | $0.16 | 10694 |  | $0.08 | $0.16 | 65J1337 | Link (http://www.newark.com/vishay-dale/crcw08051k00jneb/res-thick-film-1k-5-0-125w-0805/dp/65J1337) | 530099 |  | $0.10 | $0.20 | RMCF0805JT1K00CT-ND | Link (http://www.digikey.com/product-detail/en/RMCF0805JT1K00/RMCF0805JT1K00CT-ND/1942557)
R4,R11 | 10k |  | uCm:r_0805 |  | RMCF0805JT10K0 | 2 | $0.003 | $0.01 | 0 |  | $0.003 | $0.01 | 83R8240 | Link (http://www.newark.com/vishay-dale/crcw080510k0jneb/res-thick-film-10k-5-0-125w-0805/dp/83R8240) | 1290794 |  | $0.10 | $0.20 | RMCF0805JT10K0CT-ND | Link (http://www.digikey.com/product-detail/en/RMCF0805JT10K0/RMCF0805JT10K0CT-ND/1942577)
R5 | 4k7 |  | uCm:r_0805 |  | RMCF0805JT4K70 | 1 | $0.08 | $0.08 | 18847 |  | $0.08 | $0.08 | 65J2003 | Link (http://www.newark.com/vishay-dale/crcw08054k70jneb/res-thick-film-4k7-5-0-125w-0805/dp/65J2003) | 367345 |  | $0.10 | $0.10 | RMCF0805JT4K70CT-ND | Link (http://www.digikey.com/product-detail/en/RMCF0805JT4K70/RMCF0805JT4K70CT-ND/1942570)
R6 | 1k |  | uCm:r_0805 |  | RMCF0805JT1K00 | 1 | $0.08 | $0.08 | 10694 |  | $0.08 | $0.08 | 65J1337 | Link (http://www.newark.com/vishay-dale/crcw08051k00jneb/res-thick-film-1k-5-0-125w-0805/dp/65J1337) | 530099 |  | $0.10 | $0.10 | RMCF0805JT1K00CT-ND | Link (http://www.digikey.com/product-detail/en/RMCF0805JT1K00/RMCF0805JT1K00CT-ND/1942557)
R8 | 330E |  | uCm:r_0805 |  | RMCF0805JT330R | 1 | $0.10 | $0.10 | 4870 |  | $0.10 | $0.10 | 65T8817 | Link (http://www.newark.com/panasonic-electronic-components/erj-6geyj331v/res-thick-film-330r-5-0-125w-0805/dp/65T8817) | 203121 |  | $0.10 | $0.10 | RMCF0805JT330RCT-ND | Link (http://www.digikey.com/product-detail/en/RMCF0805JT330R/RMCF0805JT330RCT-ND/1942547)
R9 | 120E |  | uCm:r_0805 |  | RMCF0805JT120R | 1 | $0.10 | $0.10 | 7785 |  | $0.10 | $0.10 | 65T8783 | Link (http://www.newark.com/panasonic-electronic-components/erj-6geyj121v/res-thick-film-120r-5-0-125w-0805/dp/65T8783) | 140735 |  | $0.10 | $0.10 | RMCF0805JT120RCT-ND | Link (http://www.digikey.com/product-detail/en/RMCF0805JT120R/RMCF0805JT120RCT-ND/1942540)
SC6,SC7,SC9,SC10 | SCREW |  | uCm:vite_3mm |  |  | 4 | $0.00 | $0.00
SP1 | BUZZER |  | uCm:Speaker |  | PS1240P02BT | 1 | $0.27 | $0.27 | 0 |  | $0.27 | $0.27 | 17T6875 | Link (http://www.newark.com/webapp/wcs/stores/servlet/Search?catalogId=15003&langId=-1&storeId=10194&gs=true&st=PS1240P02BT) | 11446 |  | $0.72 | $0.72 | 445-2525-1-ND | Link (http://www.digikey.com/product-detail/en/PS1240P02BT/445-2525-1-ND/935930) | 0 |  | $0.71 | $0.71 | 810-PS1240P02BT | Link (http://www.mouser.com/ProductDetail/TDK/PS1240P02BT/?qs=sGAEpiMZZMsK322k1rNFfYfXmCWsjkB8iQfg2vl062k%3D)
SW1 | Reset |  | uCm:SW_PB_V_H |  | FSMRA3JH | 1 | $0.13 | $0.13 | 0 |  | $0.13 | $0.13 | 78R8645 | Link (http://www.newark.com/webapp/wcs/stores/servlet/Search?catalogId=15003&langId=-1&storeId=10194&gs=true&st=FSMRA3JH) | 4835 |  | $0.15 | $0.15 | 450-1657-ND | Link (http://www.digikey.com/scripts/DkSearch/dksus.dll?WT.z_header=search_go&lang=en&keywords=FSMRA3JH) | 13807 |  | $0.16 | $0.16 | 506-FSMRA3JH | Link (http://www.mouser.com/ProductDetail/TE-Connectivity-Alcoswitch/FSMRA3JH/)
SW2 | INT0 |  | uCm:SW_PB_V_H |  | FSMRA3JH | 1 | $0.13 | $0.13 | 0 |  | $0.13 | $0.13 | 78R8645 | Link (http://www.newark.com/webapp/wcs/stores/servlet/Search?catalogId=15003&langId=-1&storeId=10194&gs=true&st=FSMRA3JH) | 4835 |  | $0.15 | $0.15 | 450-1657-ND | Link (http://www.digikey.com/scripts/DkSearch/dksus.dll?WT.z_header=search_go&lang=en&keywords=FSMRA3JH) | 13807 |  | $0.16 | $0.16 | 506-FSMRA3JH | Link (http://www.mouser.com/ProductDetail/TE-Connectivity-Alcoswitch/FSMRA3JH/)
SW3 | INT1 |  | uCm:SW_PB_V_H |  | FSMRA3JH | 1 | $0.13 | $0.13 | 0 |  | $0.13 | $0.13 | 78R8645 | Link (http://www.newark.com/webapp/wcs/stores/servlet/Search?catalogId=15003&langId=-1&storeId=10194&gs=true&st=FSMRA3JH) | 4835 |  | $0.15 | $0.15 | 450-1657-ND | Link (http://www.digikey.com/scripts/DkSearch/dksus.dll?WT.z_header=search_go&lang=en&keywords=FSMRA3JH) | 13807 |  | $0.16 | $0.16 | 506-FSMRA3JH | Link (http://www.mouser.com/ProductDetail/TE-Connectivity-Alcoswitch/FSMRA3JH/)
U1 | TXB0104D |  | uCm:TXB0104D |  | TXB0104DR | 1 | $1.30 | $1.30 |  |  |  |  |  |  | 15409 |  | $1.59 | $1.59 | 296-21928-1-ND | Link (http://www.digikey.com/product-detail/en/TXB0104DR/296-21928-1-ND/1629281) | 12412 |  | $1.30 | $1.30 | 595-TXB0104DR | Link (http://www.mouser.com/ProductDetail/Texas-Instruments/TXB0104DR/)
U2 | LM2675-5.0 |  | uCm:SO8E |  | LM2675MX-5.0/NOPB | 1 | $3.71 | $3.71 | 2605 |  | $3.99 | $3.99 | 41K4145 | Link (http://www.newark.com/texas-instruments/lm2675mx-5-0-nopb/step-down-regulator-8-soic/dp/41K4145) | 17728 |  | $3.93 | $3.93 | LM2675MX-5.0/NOPBCT-ND | Link (http://www.digikey.com/product-detail/en/LM2675MX-5.0%2FNOPB/LM2675MX-5.0%2FNOPBCT-ND/3440121) | 4638 |  | $3.71 | $3.71 | 926-LM2675MX-5.0NOPB | Link (http://www.mouser.com/ProductDetail/Texas-Instruments/LM2675MX-50-NOPB/?qs=sGAEpiMZZMtitjHzVIkrqaeIqJaO9bXJzfwDVlMH57Q%3D)
U3 | LM2675-3.3 |  | uCm:SO8E |  | LM2675MX-3.3/NOPB | 1 | $1.80 | $1.80 | 0 |  | $1.80 | $1.80 | 41K4144 | Link (http://www.newark.com/webapp/wcs/stores/servlet/Search?catalogId=15003&langId=-1&storeId=10194&gs=true&st=LM2675MX-3.3%2FNOPB) | 6294 |  | $3.93 | $3.93 | LM2675MX-3.3/NOPBCT-ND | Link (http://www.digikey.com/product-detail/en/LM2675MX-3.3%2FNOPB/LM2675MX-3.3%2FNOPBCT-ND/3440120) | 3764 |  | $3.71 | $3.71 | 926-LM2675MX33NOPB | Link (http://www.mouser.com/ProductDetail/Texas-Instruments/LM2675MX-33-NOPB/?qs=sGAEpiMZZMtitjHzVIkrqaeIqJaO9bXJcWUe3Wul8EE%3D)
U5 | DS3231N |  | uCm:DS3231 |  | DS3231S# | 1 | $8.08 | $8.08 | 857 |  | $8.36 | $8.36 | 46W4210 | Link (http://www.newark.com/maxim-integrated-products/ds3231s/rtc-tcxo--2ppm-i2c-16soic/dp/46W4210) | 2695 |  | $8.35 | $8.35 | DS3231S#-ND | Link (http://www.digikey.com/product-detail/en/DS3231S%23/DS3231S%23-ND/1197574) | 1375 |  | $8.08 | $8.08 | 700-DS3231S# | Link (http://www.mouser.com/ProductDetail/Maxim-Integrated/DS3231S/)
U7 | ATMEGA328-AU-ND |  | uCm:TQFP32 |  | ATMEGA328-AU | 1 | $3.15 | $3.15 | 115 |  | $3.15 | $3.15 | 68T2926 | Link (http://www.newark.com/webapp/wcs/stores/servlet/Search?catalogId=15003&langId=-1&storeId=10194&gs=true&st=ATMEGA328-AU) | 7867 |  | $3.25 | $3.25 | ATMEGA328-AU-ND | Link (http://www.digikey.com/product-detail/en/ATMEGA328-AU/ATMEGA328-AU-ND/2271029) | 14855 |  | $3.16 | $3.16 | 556-ATMEGA328-AU | Link (http://www.mouser.com/ProductDetail/Atmel/ATMEGA328-AU/)
W1,W2 | EN |  | uCm:r_0805 |  |  | 2 | $0.00 | $0.00
X1 | 16MHz |  | uCm:Xtal_SMD3 |  | TSX-3225 16.0000MF09Z-AC3 | 1 | $0.59 | $0.59 |  |  |  |  |  |  | 31500 |  | $0.63 | $0.63 | SER4069CT-ND | Link (http://www.digikey.com/product-detail/en/TSX-3225%2016.0000MF09Z-AC0/SER4069CT-ND/5413938) | 23124 |  | $0.59 | $0.59 | 732-TX325-16F09Z-AC3 | Link (http://www.mouser.com/Search/Refine.aspx?Keyword=TSX-3225%2016.0000MF09Z-AC3)

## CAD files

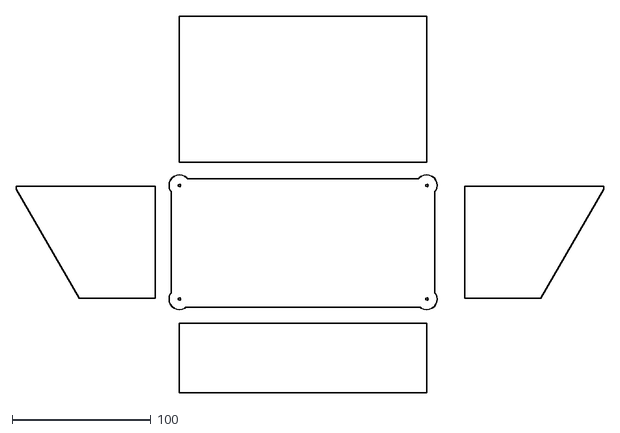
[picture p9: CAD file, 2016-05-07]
fabricate/mmM_case.dxf
423.0 x 271.3

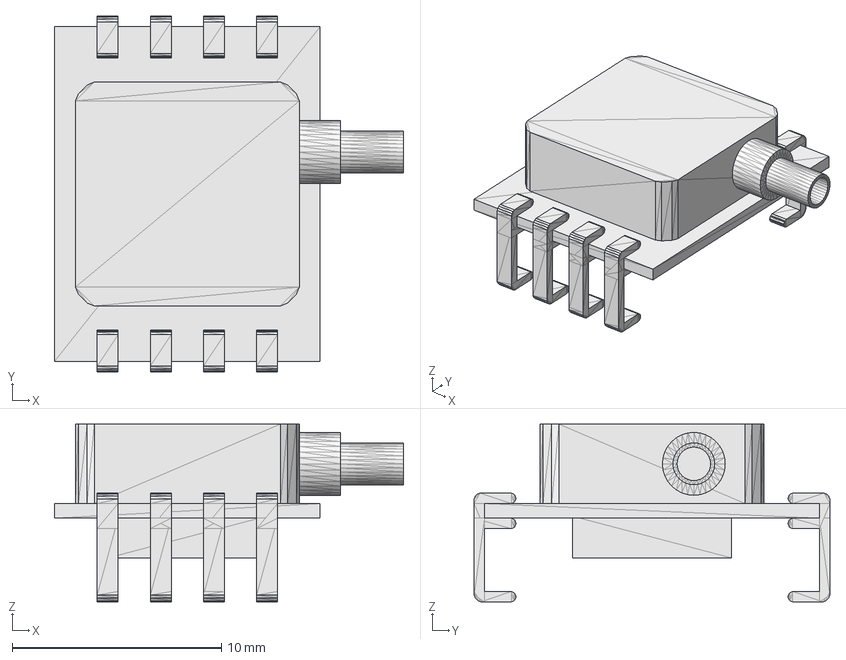
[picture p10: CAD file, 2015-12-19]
kicad/3d_modules/PrSensor.fcstd
16.7 x 17.0 x 8.50 mm

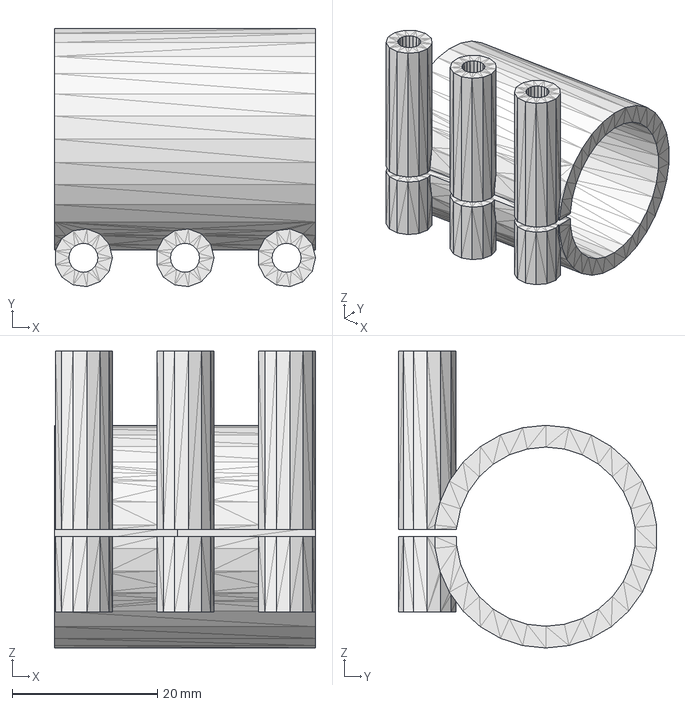
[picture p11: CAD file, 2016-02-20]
fabricate/pump_mount.step
36.0 x 35.6 x 40.9 mm

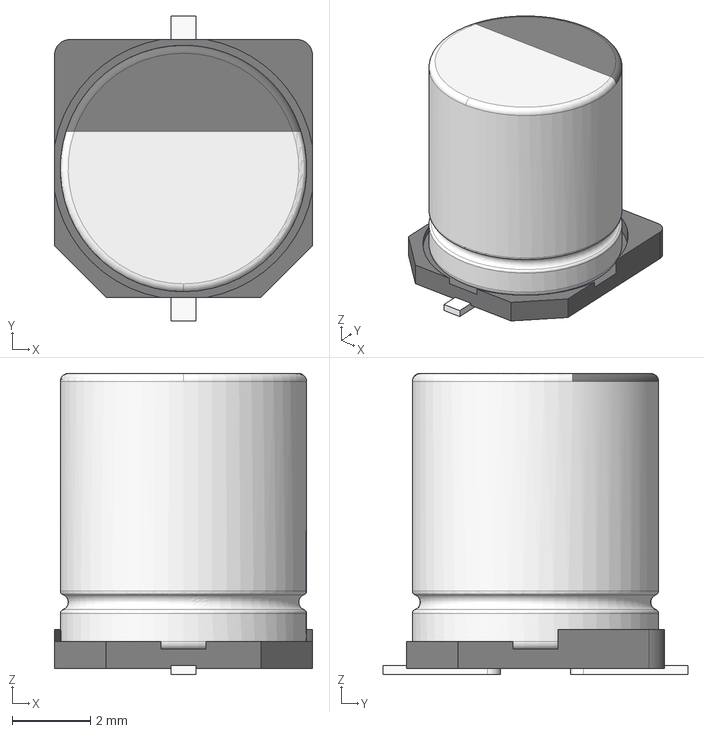
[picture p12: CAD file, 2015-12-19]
kicad/3d_modules/c_elec_6.3x7.7.step
6.60 x 7.80 x 7.70 mm

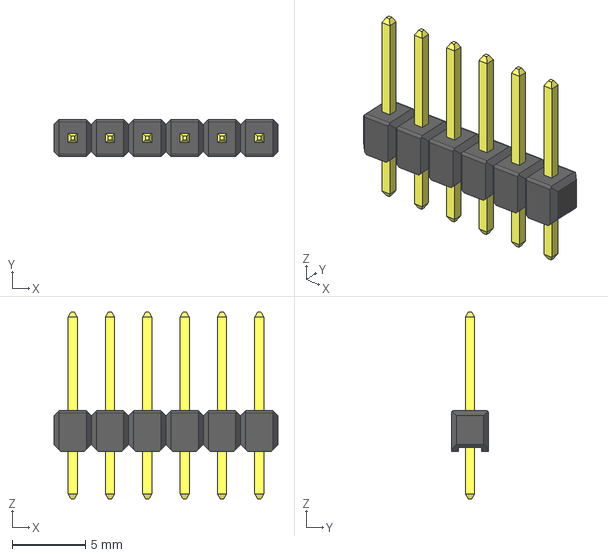
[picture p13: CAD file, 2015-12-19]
kicad/3d_modules/header_1x6_TH_2_54mm.step
15.2 x 2.54 x 12.7 mm

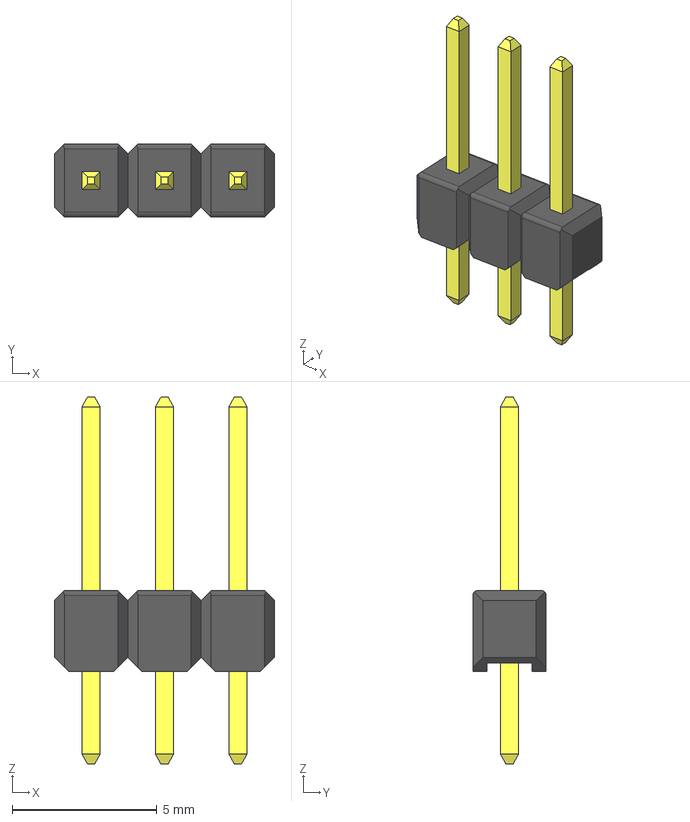
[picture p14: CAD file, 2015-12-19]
kicad/3d_modules/header_1x3_TH_2_54mm.step
7.62 x 2.54 x 12.7 mm

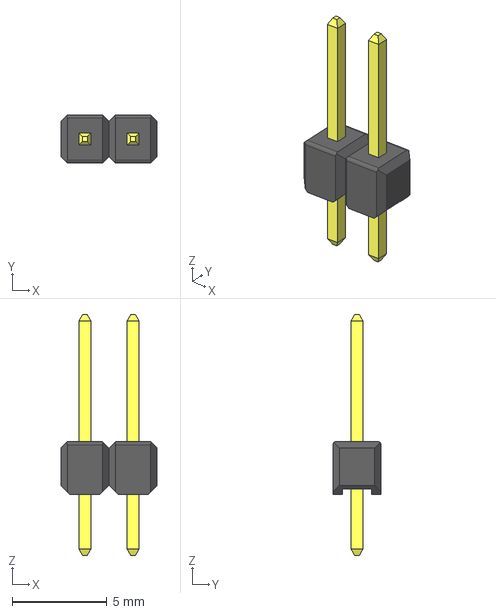
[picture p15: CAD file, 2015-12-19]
kicad/3d_modules/header_1x2_TH_2_54mm.step
5.08 x 2.54 x 12.7 mm

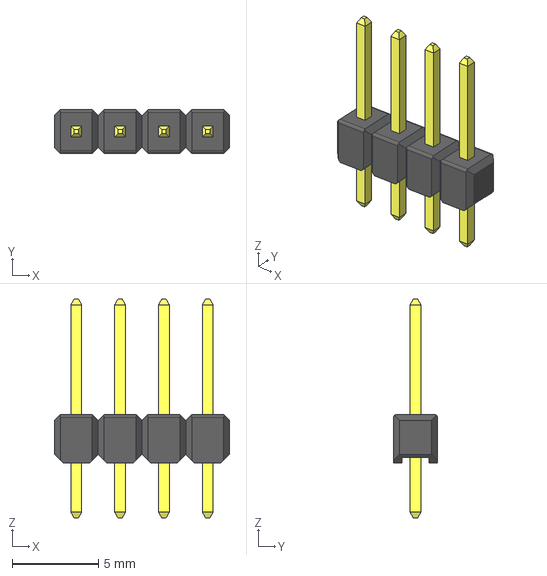
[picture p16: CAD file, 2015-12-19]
kicad/3d_modules/header_1x4_TH_2_54mm.step
10.2 x 2.54 x 12.7 mm

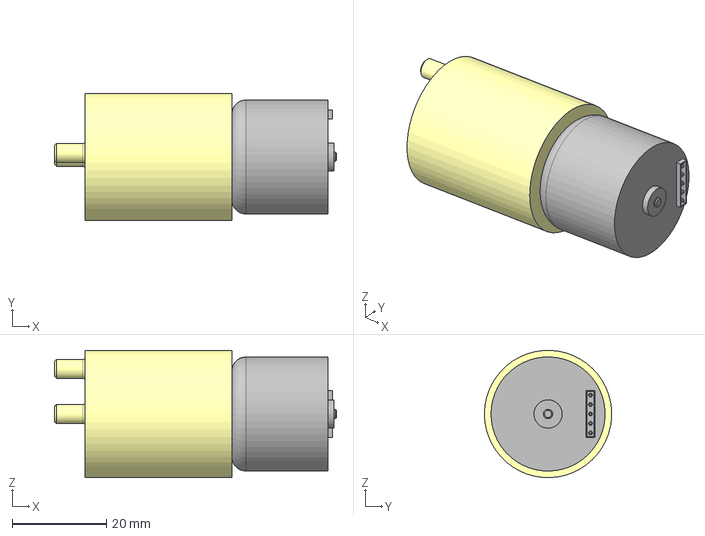
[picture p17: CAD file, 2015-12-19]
kicad/3d_modules/Pump.step
59.8 x 27.0 x 27.0 mm

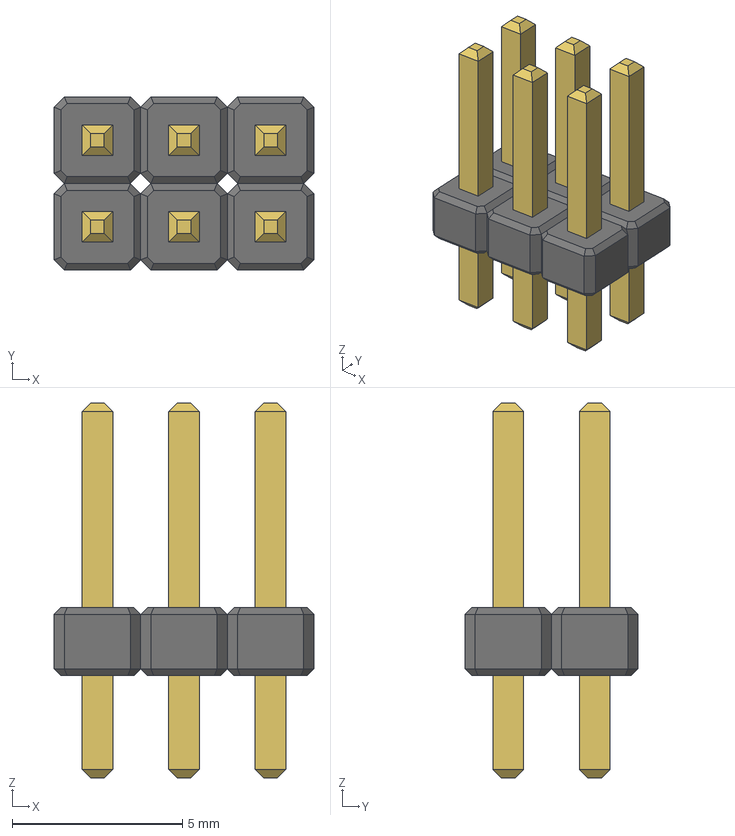
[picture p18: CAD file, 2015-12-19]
kicad/3d_modules/header_2x3_TH_2_54mm.step
7.62 x 5.08 x 11.0 mm

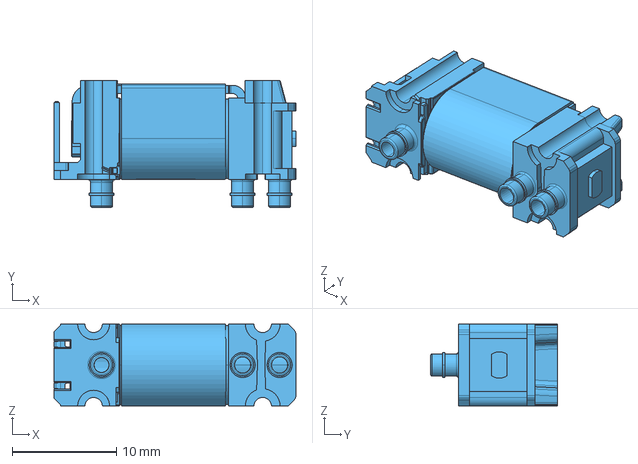
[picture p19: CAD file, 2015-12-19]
kicad/3d_modules/x-valve.fcstd
23.3 x 12.2 x 7.87 mm

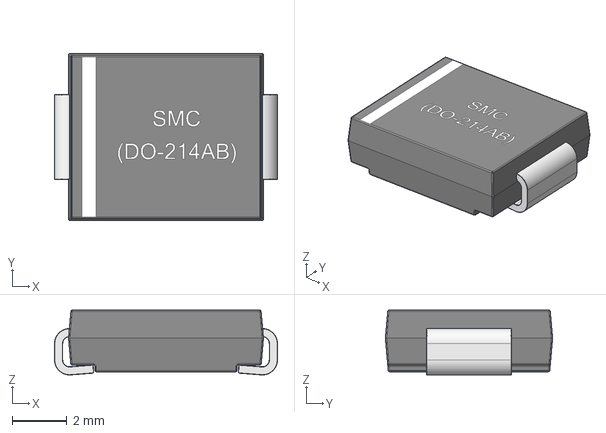
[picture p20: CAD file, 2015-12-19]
kicad/3d_modules/DO-214AB_SMC.step
8.13 x 6.10 x 2.37 mm

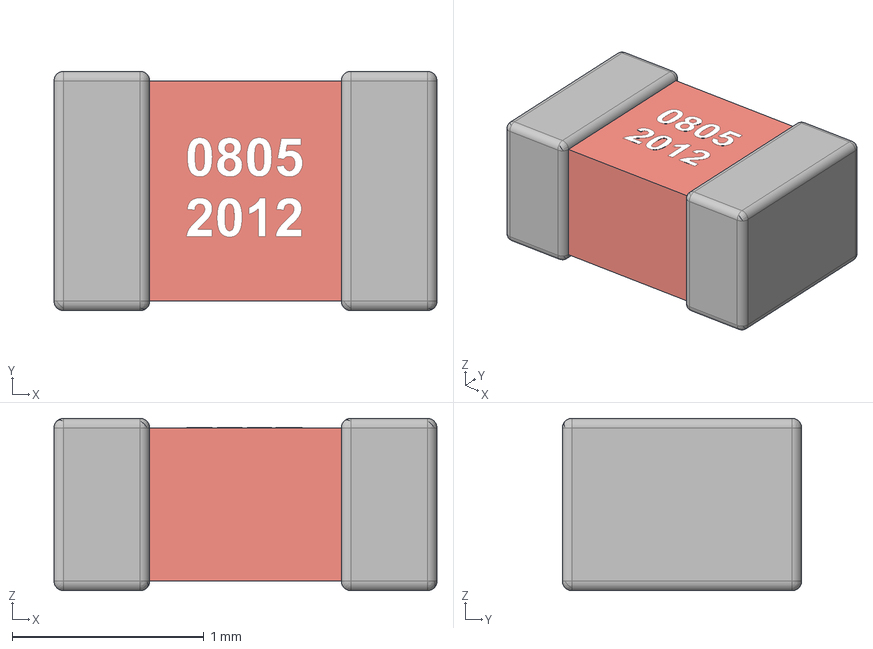
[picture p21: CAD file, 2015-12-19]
kicad/3d_modules/c_0805.step
2.00 x 1.25 x 0.9 mm

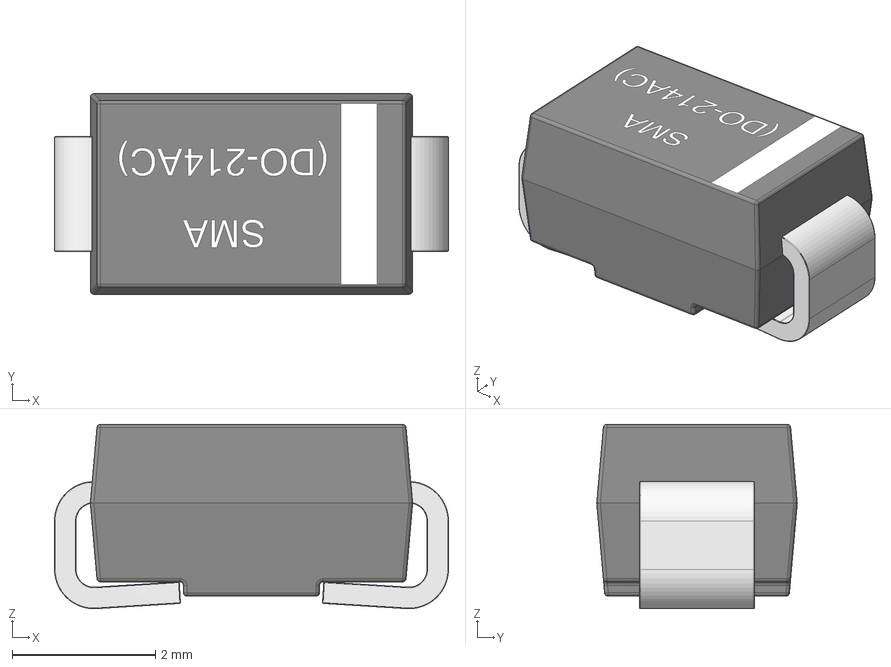
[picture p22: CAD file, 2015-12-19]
kicad/3d_modules/DO-214AC_SMA.step
5.50 x 2.80 x 2.57 mm

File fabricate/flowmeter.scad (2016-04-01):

// Sensiron SF3000 inlet/outlet adapter
inletID = 19.83;
couplerID = 24.75;
couplerLength = 24;
couplerEx = 50; // coupler should extend at 5-10cm
inch = 25.4;
hose_id = .125*inch;
cone_h = (couplerID+2)/2;

flow_exit_od = 22;
flow_exit_length = 23.5;
flow_od = 22.5;
flow_body_length=25;
flow_h = flow_body_length + 2 * flow_exit_length;

min_straight = 100;
coupler_length = flow_exit_length + min_straight;
module flow_meter(){
  $fn =99;
  cylinder(d1=flow_exit_od, d2=flow_od, h=flow_exit_length);
  translate([0, 0, flow_exit_length])cylinder(d=flow_od, h=flow_body_length);
  translate([0, 0, flow_exit_length + flow_body_length])cylinder(d2=flow_exit_od, d1=flow_od, h=flow_exit_length);
}

module hose_barb(){
    $fn = 99;
    difference(){
        union(){
            cylinder(d=hose_id,h = .25*inch);
            translate([0,0,.25*inch])cylinder(r1 = (hose_id/2)+.5, r2 =(hose_id/2) - .5, h = .25 *inch);
            translate([0,0,.35*inch])cylinder(r1 = (hose_id/2)+.5, r2 =(hose_id/2) - .5, h = .15 *inch);
        }
        translate([0,0,-1])cylinder(d=hose_id -1, h = 1.25 *inch);
    }
} 
module coupler(){
    $fn =99;
    cylinder(d=couplerID+2, h=coupler_length);
    translate([0, 0, coupler_length])cylinder(d1=couplerID+2, d2=hose_id+1.2, h=cone_h);
    translate([0, 0, coupler_length + cone_h])hose_barb();
}

module oring(){
  $fn=99;
  rotate_extrude(convexity = 10)
    translate([(couplerID-1)/2, 0, 0])
    circle(r = 1);
}

//hose_barb();

if(true){
  difference(){
    translate([0, 0, 0])coupler();
    translate([0, 0, -flow_h+flow_exit_length])scale([1.05, 1.05, 1])flow_meter();
    translate([0, 0, coupler_length])cylinder(d1=couplerID, d2=hose_id, h=cone_h);
    cylinder(d=inletID, h=coupler_length+1);
    translate([0, 0, 1])oring();
    cylinder(h=1000, d=hose_id-1, $fn=99);
  }
 }
//translate([0, 0, 0])coupler();
//  oring();

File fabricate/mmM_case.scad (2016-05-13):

inch = 25.4;

acr_t = 3.1;
screen_x = 192.96;
screen_y = 110.76;
screen_r = 7.5;
screen_d = 2 * screen_r;
screw_d = 2.5;

slant = 30;
base_y = screen_y * cos(slant);
base_x = screen_x;
h1 = 50;
h2 = h1 + screen_y * sin(slant);

rim_t = 1.2;
interior_x = 166.2 + .5;
interior_y = 101 + .5;
interior_z = rim_t + 2;
interior_z = rim_t + 1;
interior_off_x = 14 + .5 - .25;
interior_off_y = 3.5 - .25;

module slotted_cylinder(h){
  difference(){
    cylinder(r=screen_r, h = h);
    translate([-screen_r*.8, 0, -1])cube([acr_t, 100, h + 2]);
    translate([0, -screen_r*.8, -1])cube([100, acr_t, h + 2]);
    cylinder(h=h+2, d=2, $fn=20);
  }
}

module display(){
  difference(){
    translate([screen_r, screen_r, 0]) minkowski(){
      cube([screen_x - screen_d, screen_y - screen_d, rim_t/2]);
      cylinder(r=screen_r, h=rim_t/2);
    }
    translate([interior_off_x, interior_off_y, -.1])
      cube([interior_x, interior_y, interior_z]);
  }
}

module main(){
  union(){
    translate([0, sin(slant) * rim_t, h1])
      rotate(v=[1, 0, 0],a = slant) 
      display();
    
    
    difference(){
      union(){
	translate([screen_r, screen_r, 0])
	  slotted_cylinder(h = h1 + 15);
	translate([base_x - screen_r, screen_r, 0])
	  rotate(v=[0,0, 1], a=90)
	  slotted_cylinder(h = h1 + 15);
	translate([screen_r, base_y - screen_r * cos(slant), 0])
	  rotate(v=[0,0, 1], a=-90)
	  slotted_cylinder(h = h2 + 15);
	translate([base_x - screen_r, base_y - screen_r * cos(slant), 0])
	  rotate(v=[0,0, 1], a=180)
	  slotted_cylinder(h = h2 + 15);
      }
      translate([0, 0, h1])rotate(a=slant, v=[1, 0, 0])cube([1000, 1000, 1000]);
      color([1, 0, 0])translate([1, 0, h1])
	rotate(a=slant, v=[1, 0, 0])
	translate([interior_off_x, interior_off_y+1, -3 * interior_z])
	cube([interior_x, interior_y, 5 * interior_z]);
      color([1, 0, 0])translate([0, 0, h1])
	rotate(a=slant, v=[1, 0, 0])
	translate([interior_off_x, interior_off_y+1, -3 * interior_z])
	cube([interior_x, interior_y, 5 * interior_z]);
    }

    foot();
    translate([base_x - 2 * screen_r, 0, 0])foot();
    translate([base_x - 2 * screen_r, base_y - 2 * screen_r * cos(slant), 0])foot();
    translate([0, base_y - 2 * screen_r * cos(slant), 0])foot();
  }
  color([0, 1, 0])
    intersection(){
    scale([1, cos(slant), 100])
      translate([screen_r, screen_r, 0]) 
      difference(){
      minkowski(){
	cube([screen_x - screen_d, screen_y - screen_d, .0001]);
	cylinder(r=screen_r, h=rim_t);
      }
      minkowski(){
	cube([screen_x - screen_d, screen_y - screen_d, 1]);
	cylinder(r=screen_r - 1, h=rim_t);
      }
    }
    translate([0, 0, h1 - 3])rotate(a=slant, v=[1, 0, 0])cube([1000, 1000, 3]);
  }

}

module bottom1(){
  color([1, 0, 0])
  translate([screen_r, screen_r, - acr_t])minkowski(){
    cube([base_x - 2 * screen_r, base_y - 2 * screen_r, acr_t]);
    cylinder(r=screen_r, h=.0001);
  }
}
module foot(){
  translate([screen_r, screen_r, - 3 * acr_t])
    difference(){
    cylinder(r2=screen_r, r1 = screen_r * .75, h=2 * acr_t);
    cylinder(d=screw_d, h=1000, $fn=20);
    translate([0, 0, -1])
    cylinder(d=6, h=acr_t + 1, $fn=20);
  }
}
module bottom(){
  difference(){
    union(){
      translate([screen_r - 1 * acr_t, screen_r - 1 * acr_t, - acr_t])
	minkowski(){
	cube([base_x - 2 * screen_r + 2 * acr_t, 
	      base_y - 2 * screen_r + 2 * acr_t, 
	      acr_t/2]);
	cylinder(r=acr_t, h=acr_t/2);
      }
      translate([screen_r, screen_r, - acr_t])
	cylinder(r=screen_r, h=acr_t);
      translate([base_x - screen_r, screen_r, - acr_t])
	cylinder(r=screen_r, h=acr_t);
      translate([base_x - screen_r, base_y - screen_r * cos(slant), - acr_t])
	cylinder(r=screen_r, h=acr_t);
      translate([screen_r, base_y - screen_r * cos(slant), - acr_t])
	cylinder(r=screen_r, h=acr_t);
    }
    translate([screen_r, screen_r, - acr_t - 1])
      cylinder(d=screw_d, h=acr_t + 2);
    translate([base_x - screen_r, screen_r, - acr_t - 1])
      cylinder(d=screw_d, h=acr_t + 2);
    translate([base_x - screen_r, base_y - screen_r * cos(slant), - acr_t - 1])
      cylinder(d=screw_d, h=acr_t + 2);
    translate([screen_r, base_y - screen_r * cos(slant), - acr_t - 1])
      cylinder(d=screw_d, h=acr_t + 2);
  }
}

module side(){
  color([1, 0, 0])
    rotate(a=90, v=[0, -1, 0])
    intersection(){
    linear_extrude(height=acr_t)
      polygon(points=[[0, 0], [0, base_y], [h2, base_y], [h1, 0]]);
    translate([-100, screen_r + .5, -100])cube([200, base_y - 2 * screen_r, 200]);
  }
}

module front(){
  translate([screen_r, screen_r - acr_t, 0])cube([base_x - 2 * screen_r, acr_t, h1]);
}

module back(){
  translate([screen_r, base_y - screen_r + acr_t, 0])cube([base_x - 2 * screen_r, acr_t, h2 - sin(slant) * acr_t]);
}

//main();
//translate([screen_r - acr_t, 0, 0])side();
//translate([base_x - screen_r + acr_t, 0, 0])side();
// front();
// back();

laser_cut = false;
if(laser_cut){
  projection()bottom();
  projection()translate([-10, 0, 0])rotate(a=-90, v=[0, 1, 0])side();
  projection()translate([base_x + 20, 0, 0])rotate(a=90, v=[0, 1, 0])side();
  projection()translate([0, -10, -2 * acr_t])rotate(a=90, v=[1, 0, 0])front();
  projection()translate([0, base_y + 10, base_y - acr_t])rotate(a=-90, v=[1, 0, 0])back();
 }
 else{
   main();
   translate([screen_r - acr_t, 0, 0])side();
   translate([base_x - screen_r + acr_t, 0, 0])side();
   front();
   back();
   bottom();
 }
color([1, 0, 1])translate([19, 9, 30])scale(.282)linear_extrude(height=1.5)import("mmM_board_outline.dxf");

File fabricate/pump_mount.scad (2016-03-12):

pump_d = 24.7;
pump_D = 27.5;
wall_t = 3;
pump_h = 20;
screw_sep = 14;
screw_head_d = 8;
screw_h = 36;
pump_center_z = pump_d/2 + wall_t - 3;
slit_t = 1;

module pump(){
translate([-pump_h/2, pump_d/2 + wall_t, pump_center_z]) 
  rotate(a=90, v=[0, 1, 0])
  translate([0, 0, -1])
  {
    cylinder(d=pump_d, h=pump_h + 2);
    translate([0, 0, -pump_h])cylinder(d=pump_D, h=pump_h + 2);
  }
}

module p_clamp(){
  difference(){
    union(){
      difference(){
	{
	  translate([-1.25 * pump_h, pump_d/2 + wall_t, pump_center_z]) 
	    rotate(a=90, v=[0, 1, 0])
	    cylinder(d=pump_d + 2 * wall_t, h=2 * screw_sep + screw_head_d);
	}
	translate([1, 0, 0])pump();
      }
    
    
      difference(){
	union(){
	  for(i=[-1.5, -.5, .5]){
	    translate([i * screw_sep, -1, pump_d/5])
	      cylinder(d=screw_head_d, h=screw_h);
	  }
	}
	pump();
	cube([pump_h + 2, 100, slit_t]);
      }
    }
    // slot
    translate([-pump_h/2 - 100, -20, pump_center_z])
      cube([pump_h + 2 + 100, pump_d/2 + wall_t + 20, 1]);

    for(i=[-1.5, -.5, .5]){
      translate([i * screw_sep, -1, pump_d/5])
	translate([0, 0, -1])cylinder(d=4, h=screw_h + 2, $fn=20);
    }
  }
}
translate([0, -pump_d/2 - wall_t, -pump_d/2 - wall_t])
color([1, 0 ,0])
p_clamp();

if(false){
  translate([1.5, 21.6, 25])
    rotate(a=180, v=[1, 0, 0])
    import("board.stl");
  
  translate([-6.5, 18, 20.5])
    rotate(a=180, v=[1, 0, 0])
    import("pump.stl");
}

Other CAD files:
kicad/3d_modules/cms_so16.step
kicad/3d_modules/LED_SMD_Mini_top.step
kicad/3d_modules/batt-02.step
kicad/3d_modules/C0603.step
fabricate/pump_mount.stl
kicad/3d_modules/C_2917.step
kicad/3d_modules/PowerJack-2_5x5_7mm.step
kicad/3d_modules/SOT223.step
kicad/3d_modules/SW_0773.step
kicad/3d_modules/cap_al_el_8x10.step
kicad/3d_modules/cms_so14.step
kicad/3d_modules/cms_so8.step
kicad/3d_modules/ind_WE_smd2-LC75.step
kicad/3d_modules/pump.fcstd
kicad/3d_modules/speaker-WST-1203UX.step
kicad/3d_modules/tqfp32.step
kicad/3d_modules/xtal_tsx-3225-1.step

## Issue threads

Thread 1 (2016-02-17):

### ISSUE TITLE
Reset button should be separate from the other buttons

### ISSUE THREAD

**Issue by osbock** [wyolum/mmM#1]
It's too easy to try all the buttons, and the reset looks just like another button.

**Comment by Anool** [comment]
We could use right angle switches with long actuators for the regular buttons, and a shorter stem for the RESET.
Or, we can use a horizontal switch for RESET (not right angle). But this may not be accessible from outside the case. Suggestions on how to solve this.

**Comment by osbock** [comment]
Maybe it's completely solved by the case. A recessed button (perhaps poked with a paper clip) versus exterior protruding buttons would do the trick!

**Comment by Anool** [comment]
+1. That solves it. I'm closing this issue. We can open another one regarding features that the case must have. Reset button recessed, slot for coin battery, Slots for cables etc.

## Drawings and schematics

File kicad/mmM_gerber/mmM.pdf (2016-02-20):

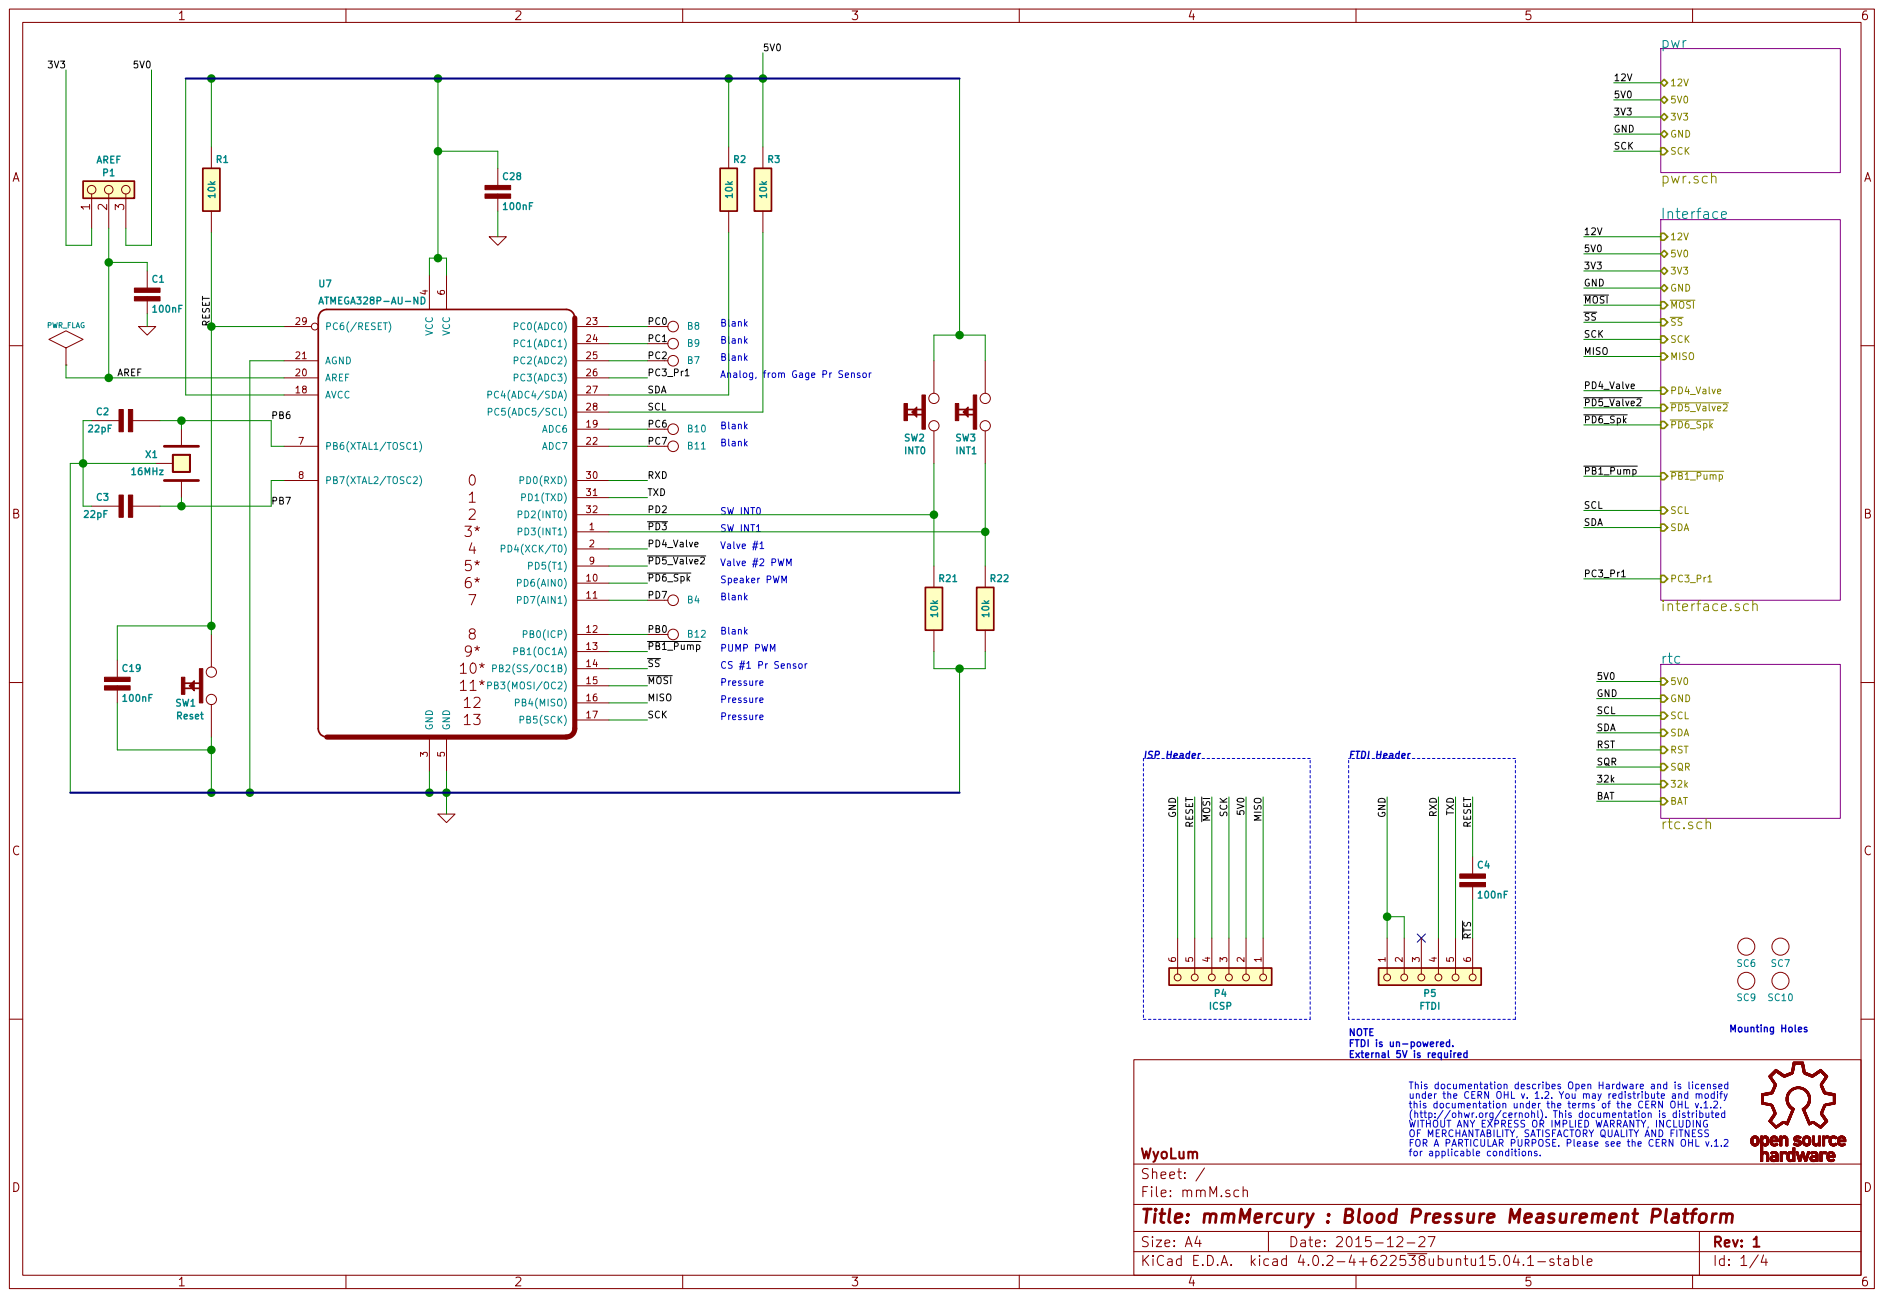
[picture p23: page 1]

3V3 Pressure Pressure Pressure CS #1 Pr Sensor PUMP PWM

6 PB6(XTAL1/TOSC1) 7 PB7(XTAL2/TOSC2) 8 PD5(T1) 9 PD6(AIN0) 10 AREF 20 PD0(RXD) 30 PD7(AIN1) 11 AGND 21 PD1(TXD) 31 PB0(ICP) 12 ADC7 22 PD2(INT0) 32 PB1(OC1A) 13 PC0(ADC0) 23 PB2(SS/OC1B) 14 PC1(ADC1) 24 PB3(MOSI/OC2) 15 PC2(ADC2) 25 PB4(MISO) 16 PC3(ADC3) 26 PB5(SCK) 17 PC4(ADC4/SDA) 27 AVCC 18 PC5(ADC5/SCL) 28 ADC6 19 PC6(/RESET) 29 U7ATMEGA328P-AU-ND

SCL SSMOSI SCK MISO 0

Valve #2 PWM
Blank Blank Speaker PWM

FTDI is un-powered. External 5V is required

This documentation describes Open Hardware and is licensed under the CERN OHL v. 1.2. You may redistribute and modify
this documentation under the terms of the CERN OHL v.1.2. (http://ohwr.org/cernohl). This documentation is distributed WITHOUT ANY EXPRESS OR IMPLIED WARRANTY, INCLUDING OF MERCHANTABILITY, SATISFACTORY QUALITY AND FITNESS

File: mmM.sch Sheet: / WyoLum

FOR A PARTICULAR PURPOSE. Please see the CERN OHL v.1.2
for applicable conditions.

Id: 1/4 Title: mmMercury : Blood Pressure Measurement Platform

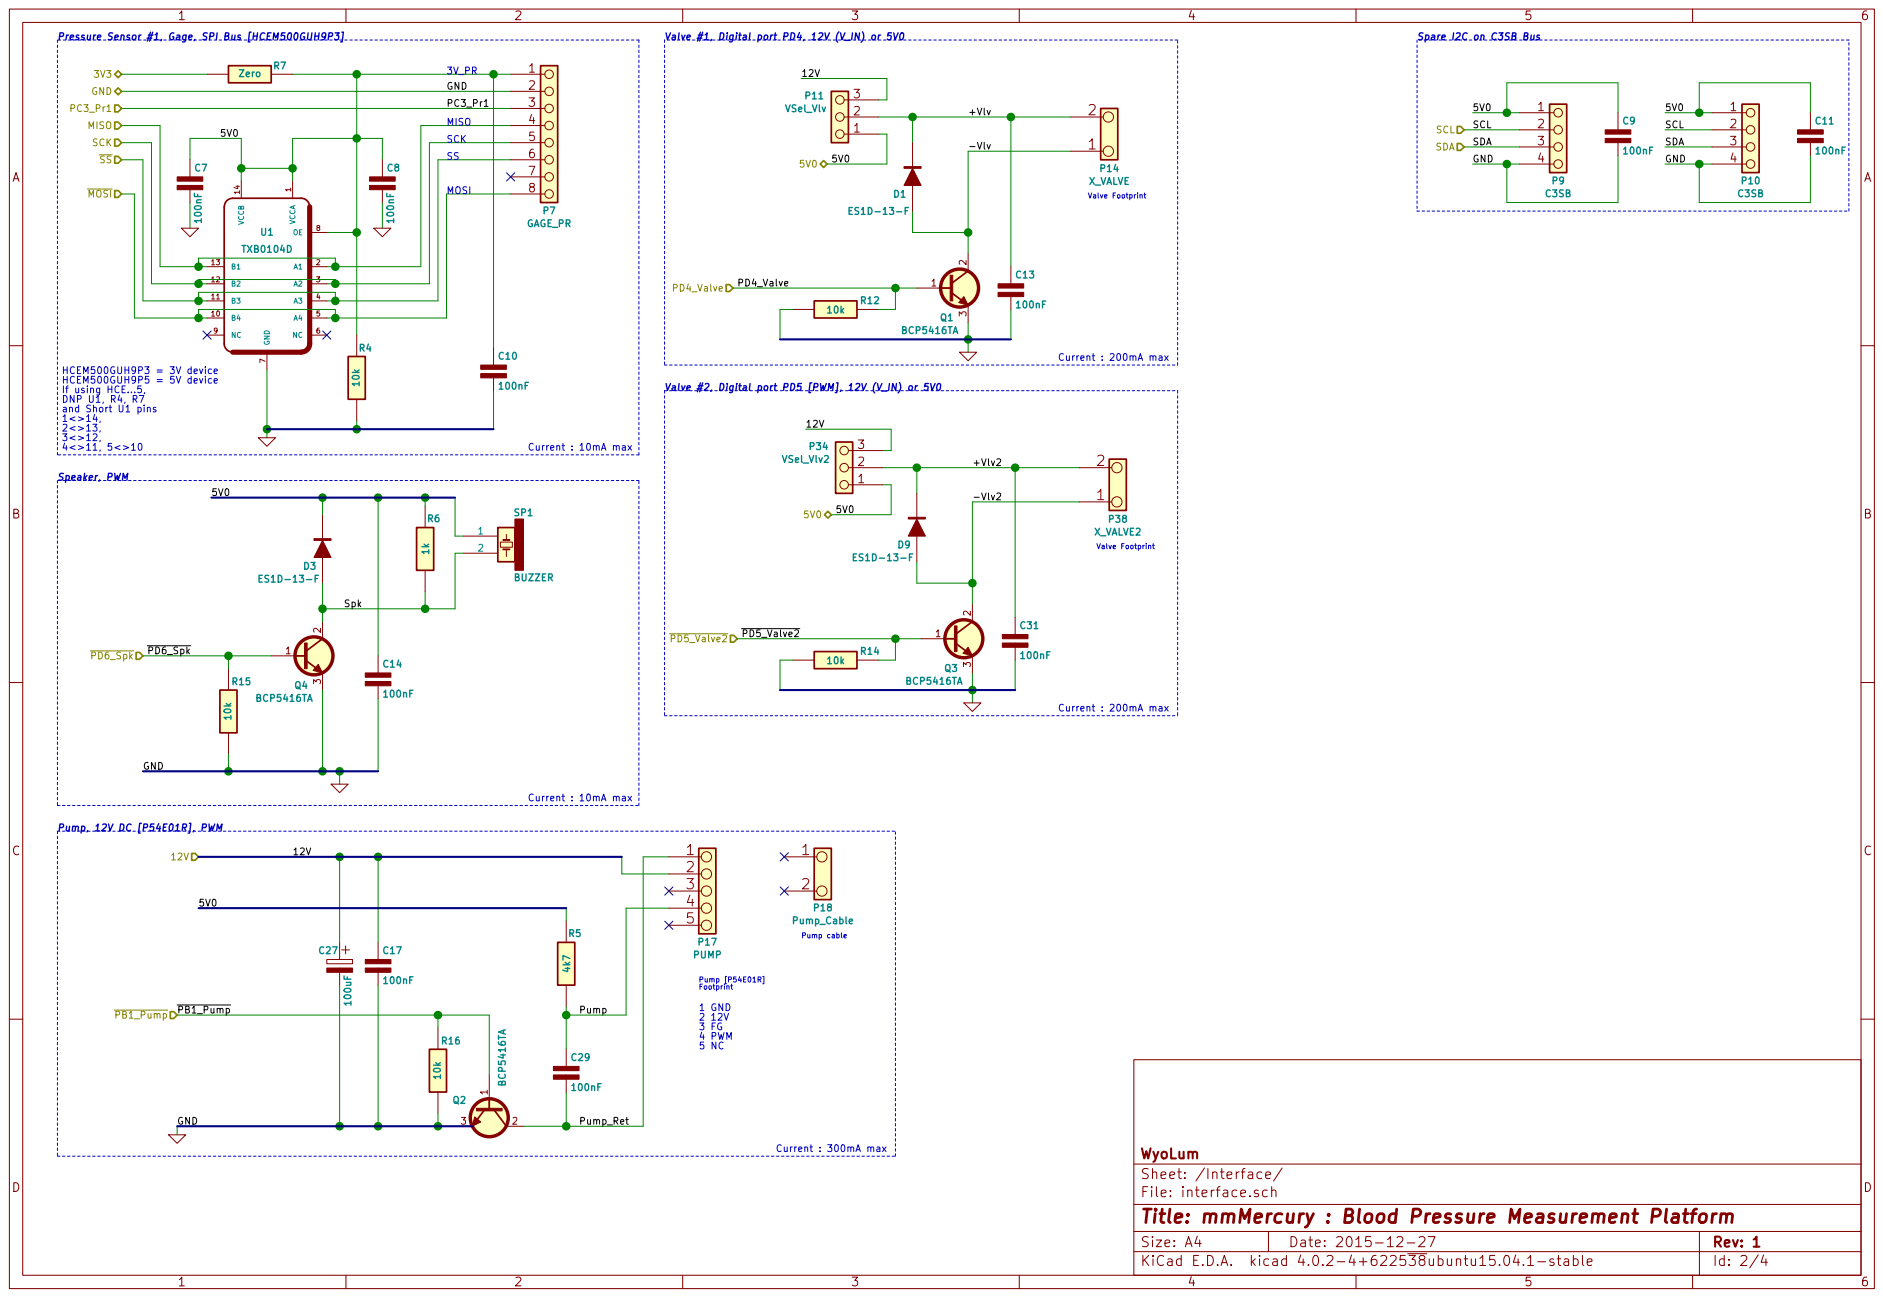
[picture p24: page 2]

PC3_Pr1 GND | 2 3 4

SCK | 5

Current : 200mA max

If using HCE...5, DNP U1, R4, R7

File: interface.sch Sheet: /Interface/ WyoLum

Id: 2/4 Title: mmMercury : Blood Pressure Measurement Platform

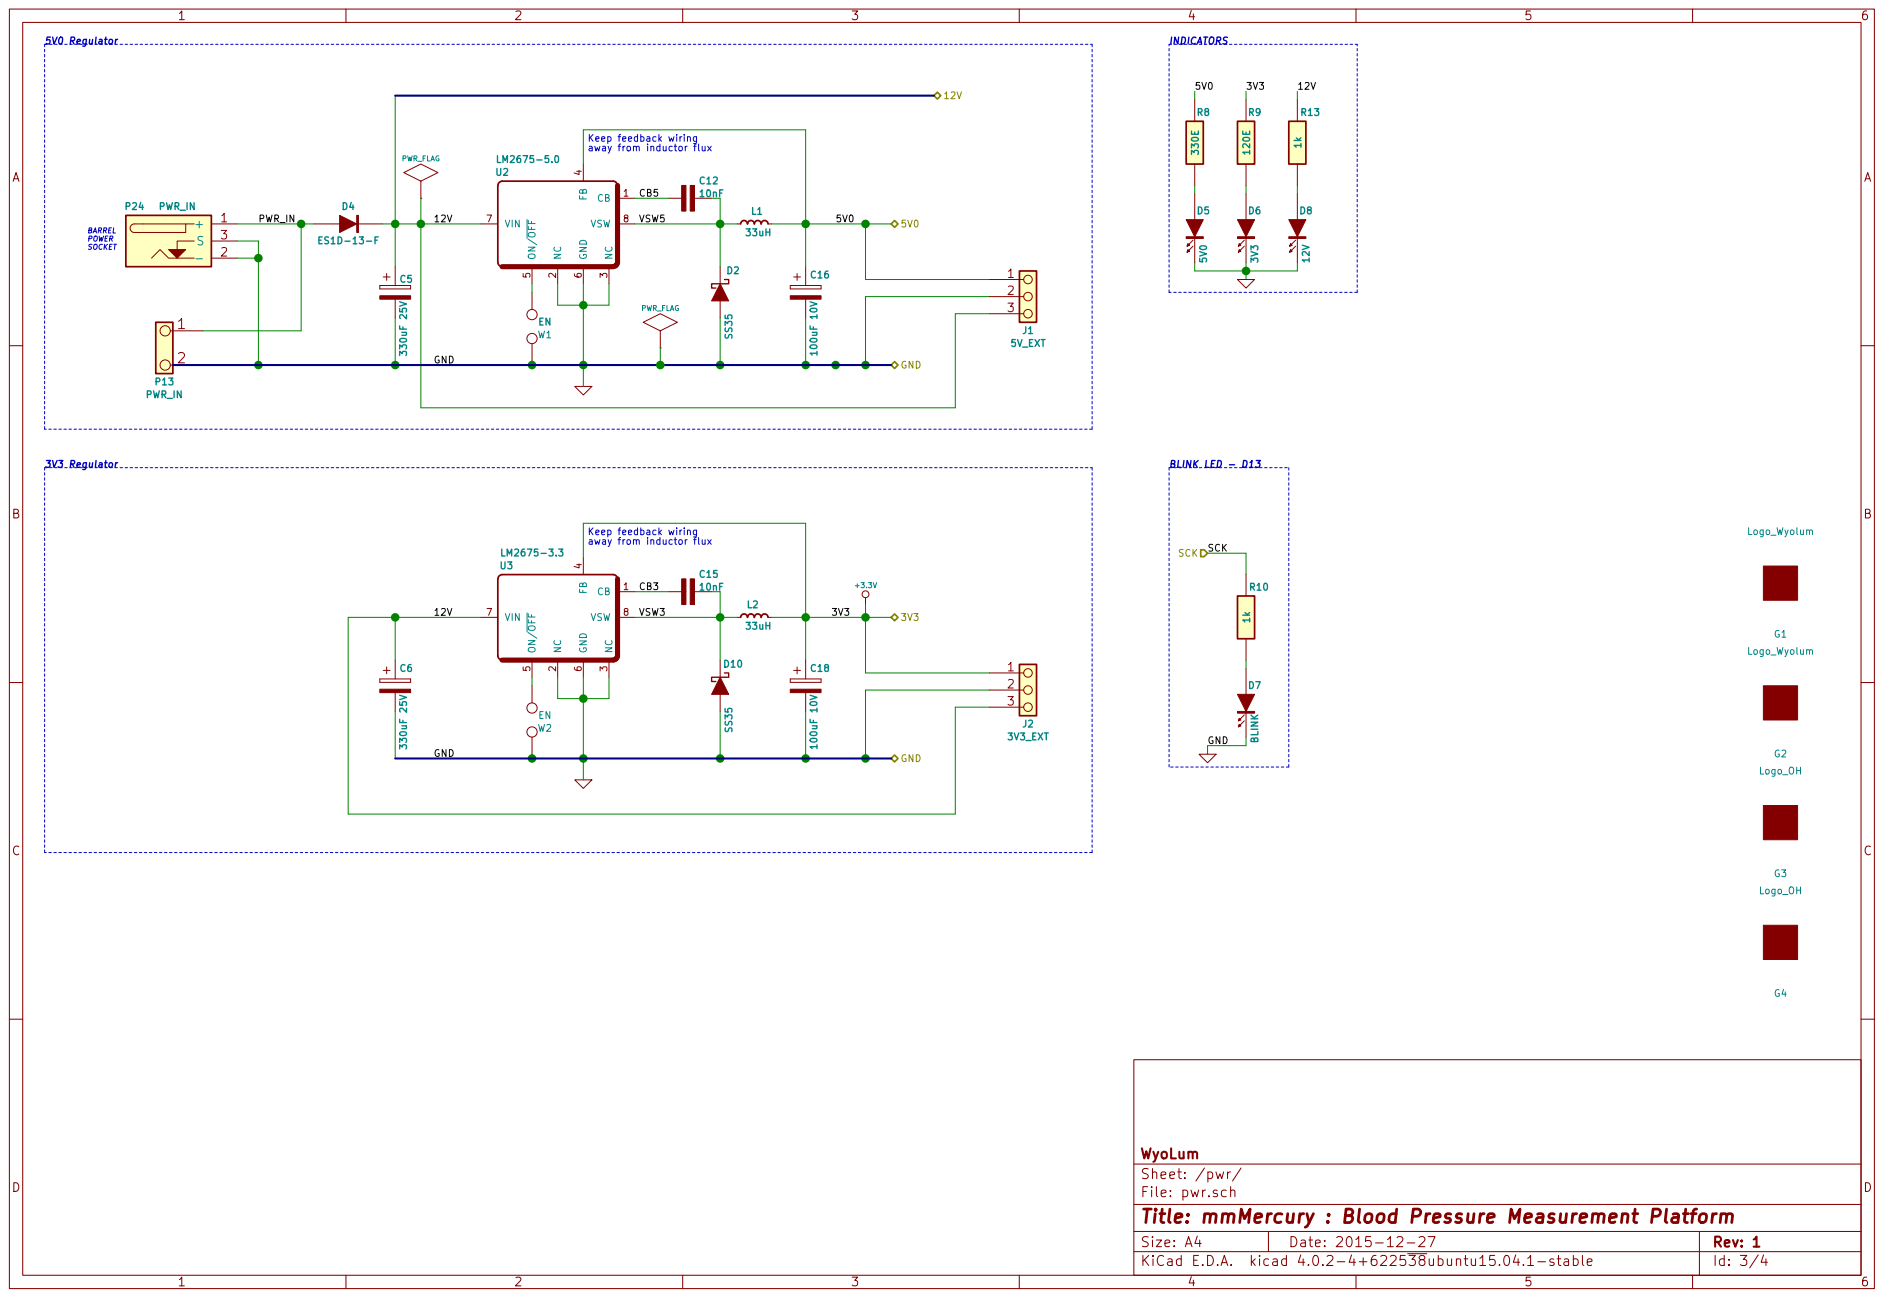
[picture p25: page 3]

INDICATORS BLINK LED - D13 GND

away from inductor flux W1 EN

away from inductor flux W2 EN

WyoLum
Sheet: /pwr/
File: pwr.sch
Id: 3/4 Title: mmMercury : Blood Pressure Measurement Platform

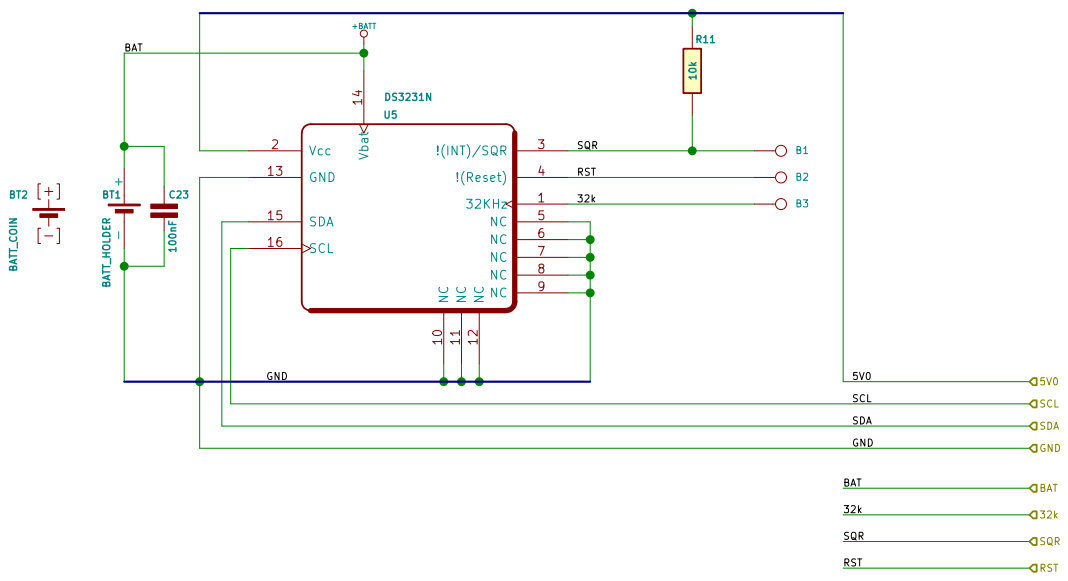
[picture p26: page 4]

File: rtc.sch Sheet: /rtc/ WyoLum

Id: 4/4 Title: mmMercury : Blood Pressure Measurement Platform

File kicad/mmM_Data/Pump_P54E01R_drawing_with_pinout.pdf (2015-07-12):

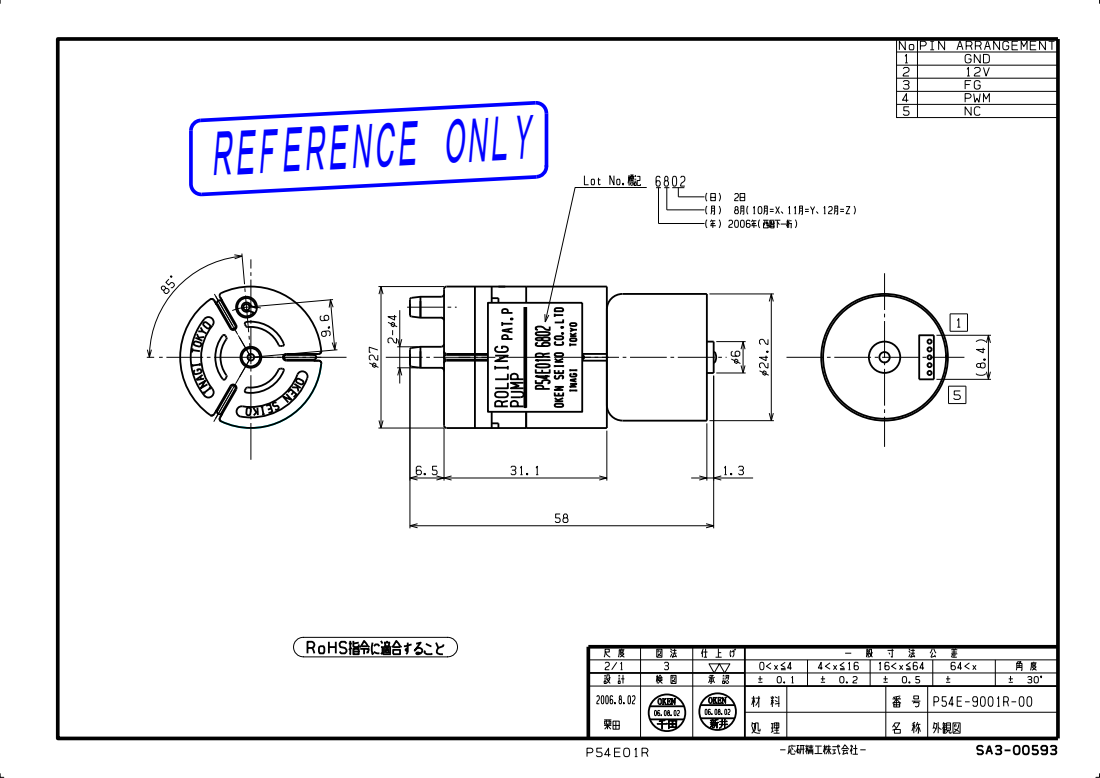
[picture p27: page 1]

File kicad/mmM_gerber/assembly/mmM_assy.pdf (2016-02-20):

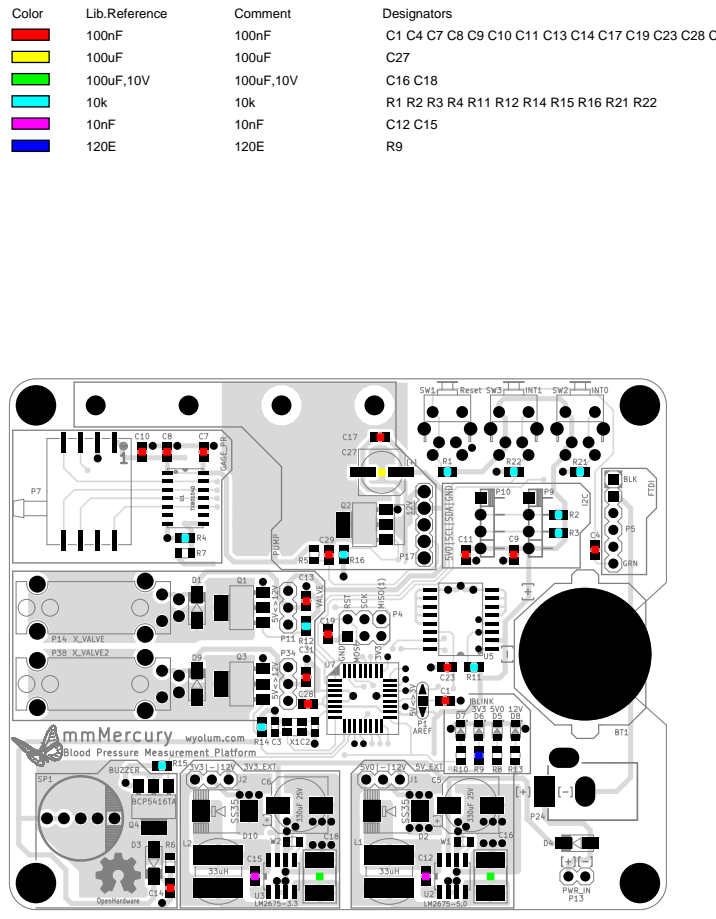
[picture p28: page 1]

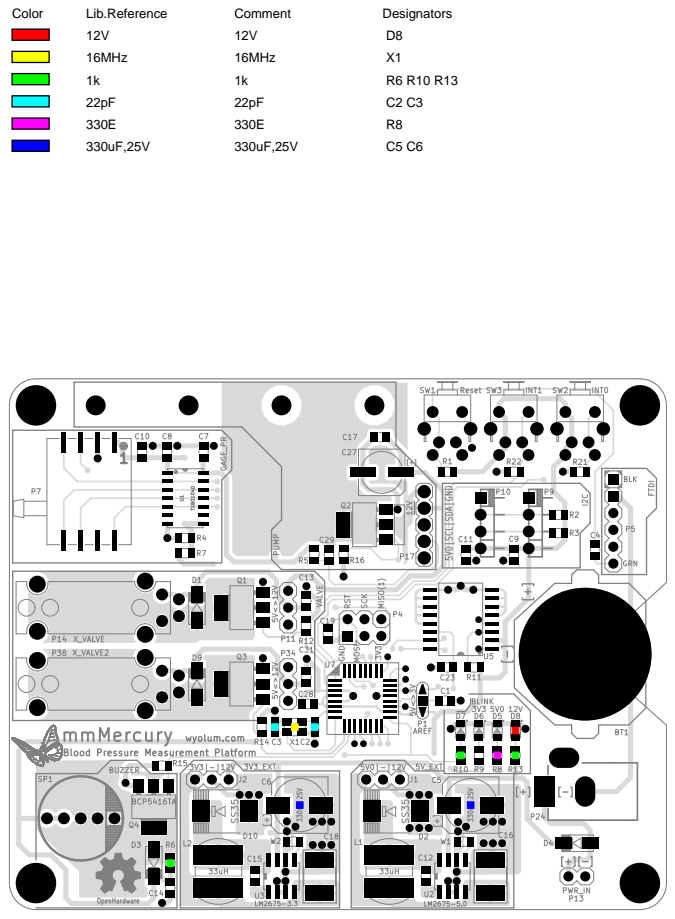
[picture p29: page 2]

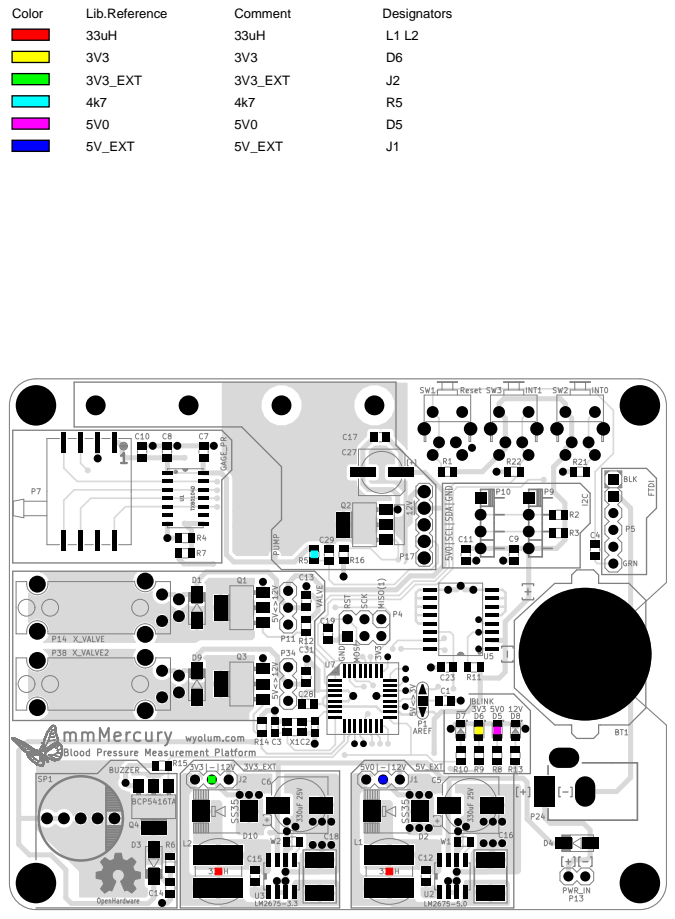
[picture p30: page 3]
Color; Lib.Reference; Comment; Designators; 3V3_EXT; 5V_EXT

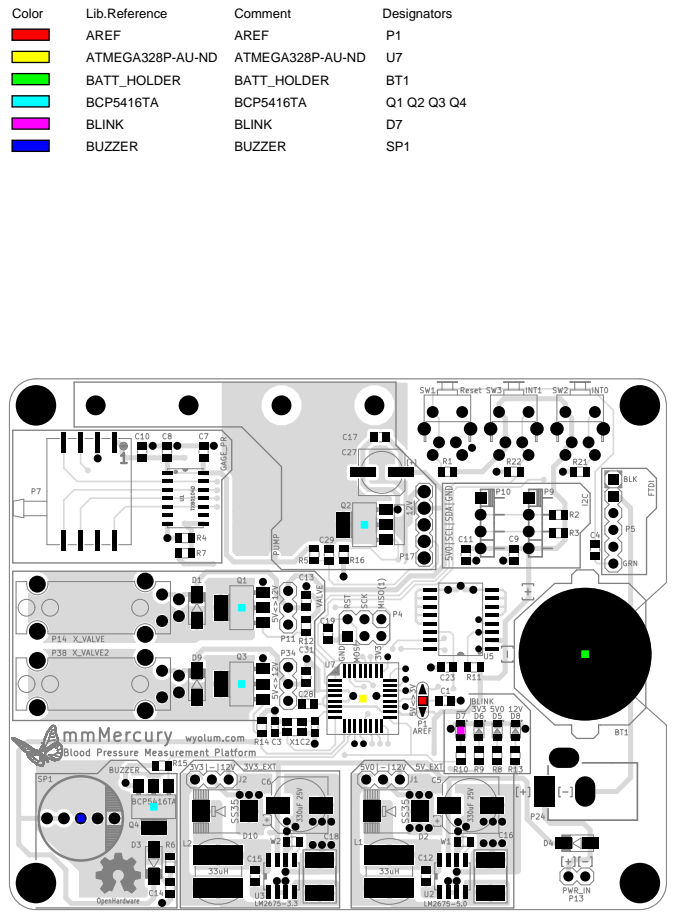
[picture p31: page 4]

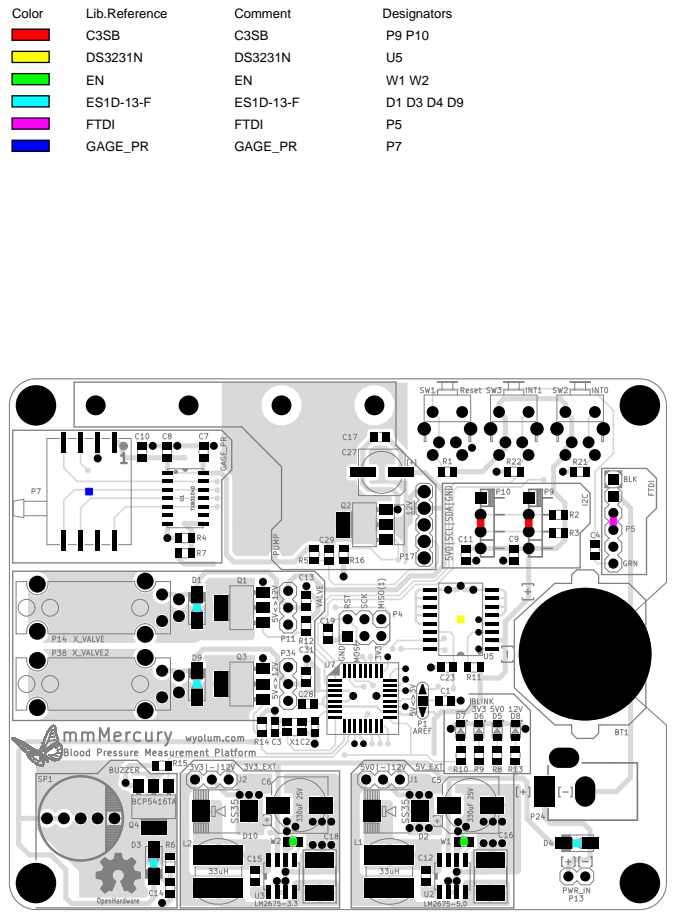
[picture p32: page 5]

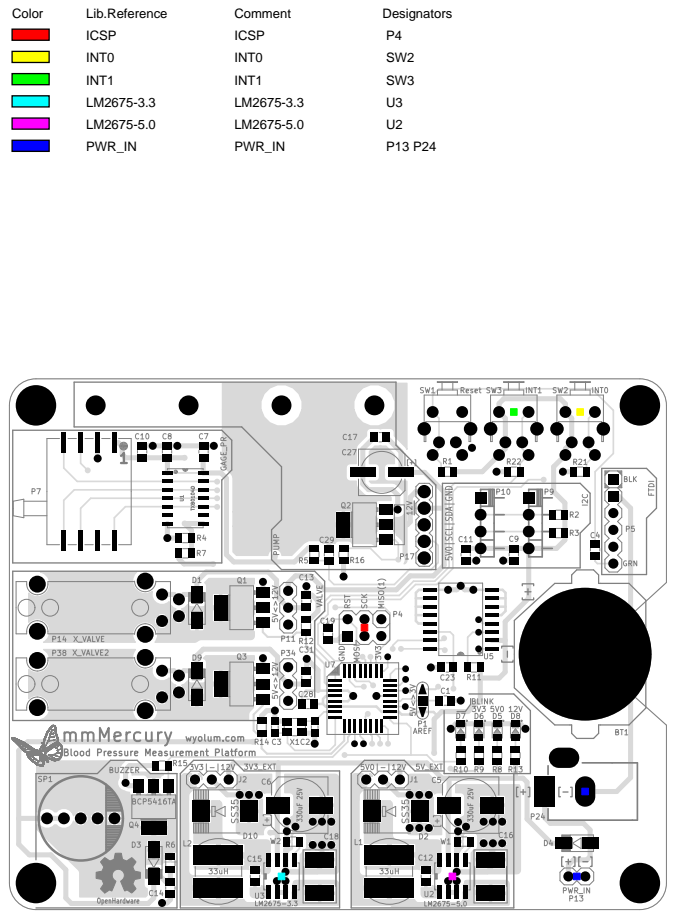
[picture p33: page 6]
Color; Lib.Reference; Comment; Designators; ICSP; INT0; INT1; PWR_IN

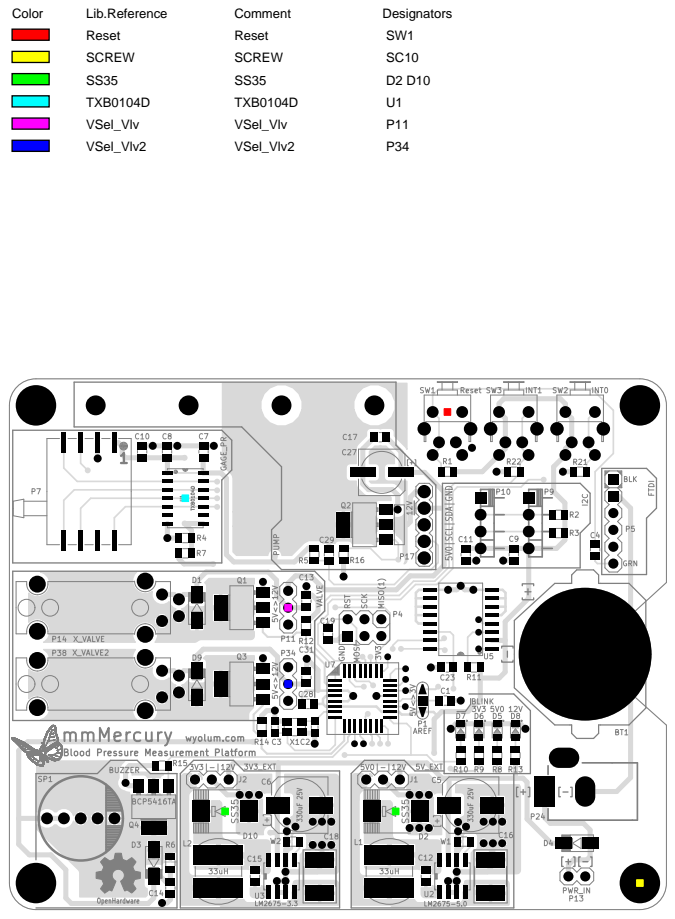
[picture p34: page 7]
Color; Lib.Reference; Comment; Designators; Reset; SCREW; TXB0104D; VSel_Vlv; VSel_Vlv2

Color; Lib.Reference; Comment; Designators; X_VALVE; X_VALVE2; Zero


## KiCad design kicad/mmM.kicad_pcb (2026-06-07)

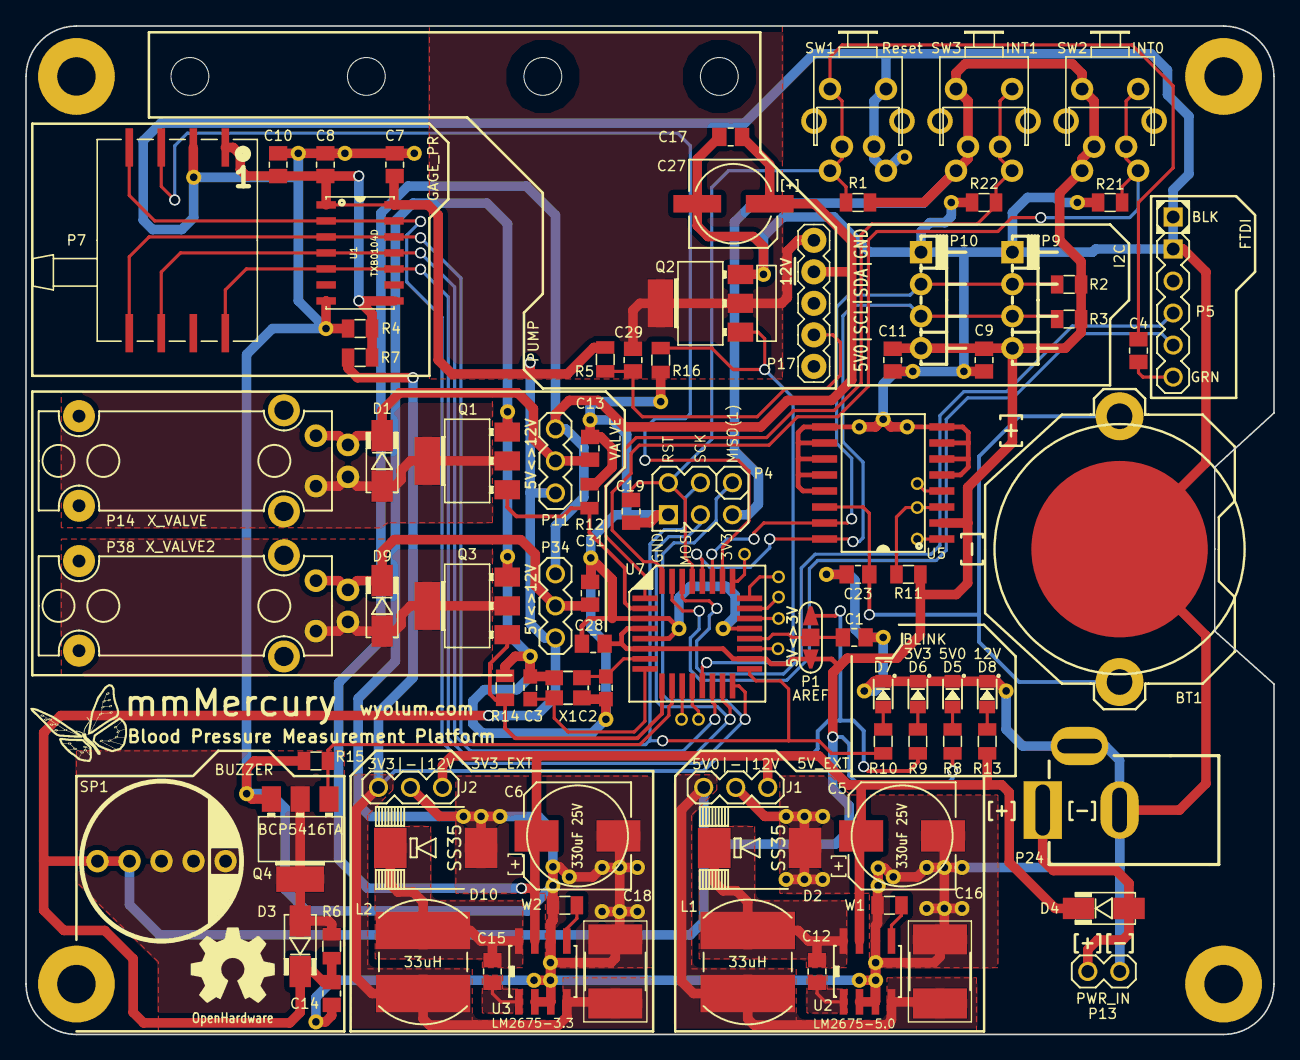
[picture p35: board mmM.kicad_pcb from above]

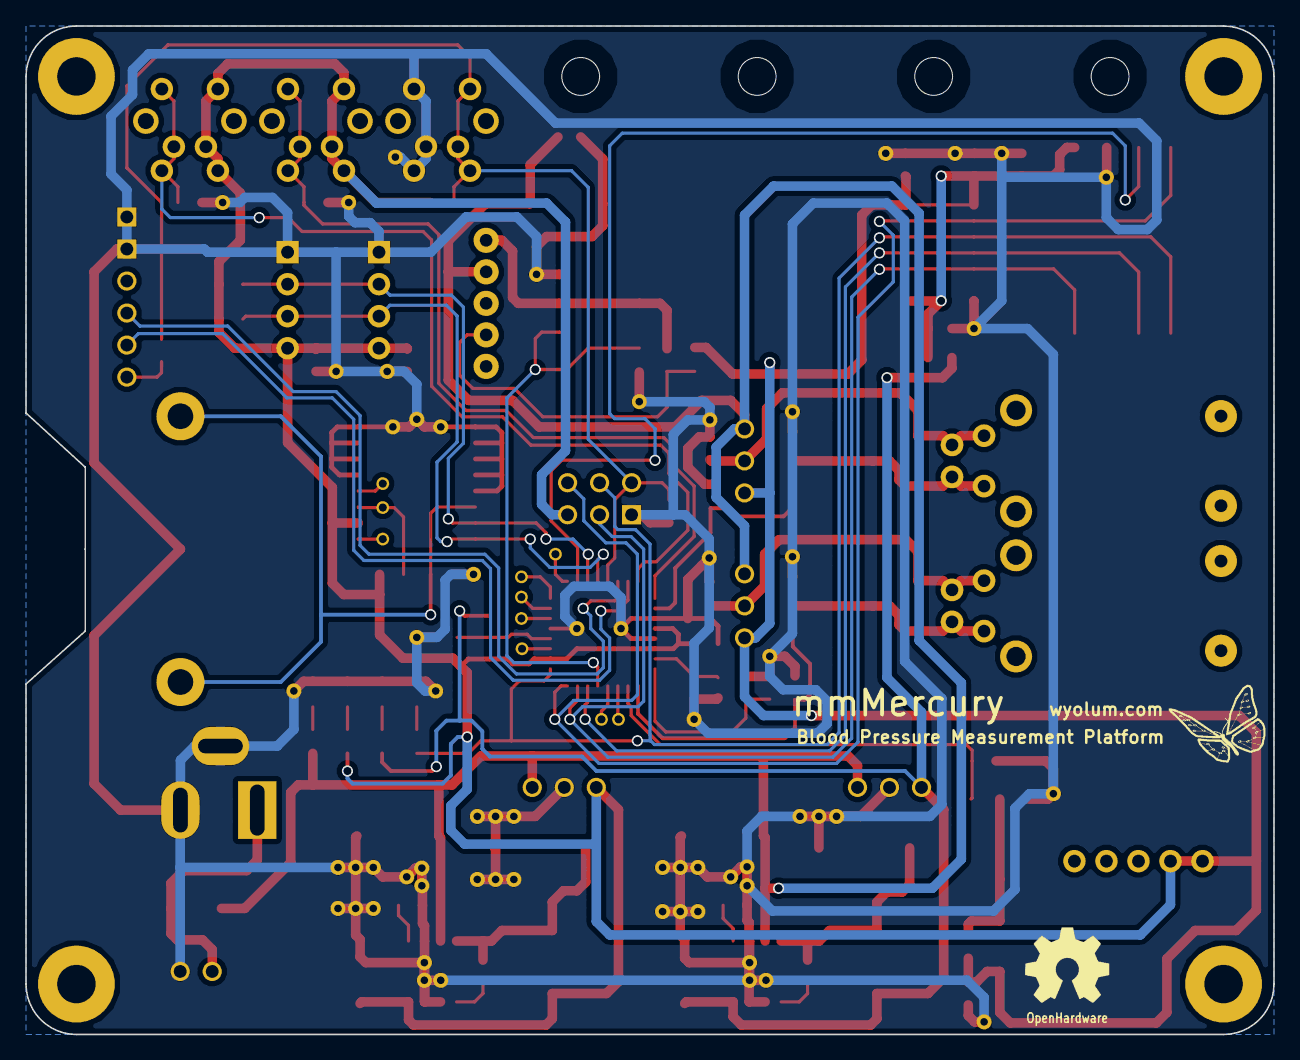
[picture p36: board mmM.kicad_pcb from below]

Board: 2 copper layers, 99.0 x 80.0 mm, 167 parts (2 on the bottom side), 53 nets.

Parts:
B1, B2, B3: I_O
B4, B12: PB0; I_O
B7, B9: PC1; I_O
B8: PC0; I_O
B10: PC6; I_O
B11: PC7; I_O
BT1: BATT_HOLDER; CR2032
C1, C4, C7, C8, C9, C10, C11, C13, C14, C17, C19, C23, C28, C29, C31: 100nF; c_0805
C2, C3: 22pF; c_0603
C5, C6: 330uF 25V; C_ELCO_SMD_8x10
C12, C15: 10nF; c_0805
C16, C18: 100uF 10V; C_2917_HandSoldering
C27: 100uF; C_ELCO_SMD
D1, D3, D4, D9: ES1D-13-F; diode-DO214AC
D2, D10: SS35; DO-214AB
D5: 5V0; led_0805
D6: 3V3; led_0805
D7: BLINK; led_0805
D8: 12V; led_0805
G1, G2: Logo_Wyolum; Logo-WL3
G3, G3#2, G4: Logo_OH; OSHW_6mm
J1: 5V_EXT; Header_3
J2: 3V3_EXT; Header_3
L1, L2: 33uH; Choke_SMD_Wuerth-784775133
P1: AREF; ShortLink2
P4: ICSP; Header_ISP
P5: FTDI; Header_FTDI
P7: GAGE_PR; HCEM500GUH9P3
P9, P10: C3SB; pin_strip_4-90
P11: VSel_Vlv; Header_3
P13: PWR_IN; Header_2
P14: X_VALVE; X_Valve_2
P17: PUMP; Pump_P54E01R_03
P24: PWR_IN; JACK_ALIM
P34: VSel_Vlv2; Header_3
P38: X_VALVE2; X_Valve_2
Q1, Q2, Q3, Q4: BCP5416TA; SOT223
R1, R2, R3, R4, R11, R12, R14, R15, R16, R21, R22: 10k; r_0805
R5: 4k7; r_0805
R6, R10, R13: 1k; r_0805
R7: Zero; r_0805
R8: 330E; r_0805
R9: 120E; r_0805
REF1, REF2, REF3, REF4, REF5, REF6, REF7, REF8, REF9, REF10, REF11, REF12, REF13, REF14, REF15, REF16, REF17, REF18, REF19, REF20, REF21, REF22, REF23, REF24, REF25, REF26, REF27, REF55, REF56, REF57, REF58, REF60, REF61, REF62: via01
REF28, REF29, REF30, REF31, REF32, REF33, REF34, REF35, REF36, REF37, REF38, REF39, REF40, REF41, REF42, REF43, REF44, REF45, REF46, REF47, REF48, REF49, REF50, REF51, REF52, REF53, REF54, REF59: via01; via_th
SC6, SC7, SC9, SC10: SCREW; vite_3mm
SP1: BUZZER; Speaker
SW1: Reset; SW_PB_V_H
SW2: INT0; SW_PB_V_H
SW3: INT1; SW_PB_V_H
U1: TXB0104D
U2: LM2675-5.0; SO8E
U3: LM2675-3.3; SO8E
U5: DS3231N; DS3231
U7: ATMEGA328P-AU-ND; TQFP32
W1, W2: EN; r_0805
X1: 16MHz; Xtal_SMD3

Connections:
+3.3V: C18.1, J2.1, L2.2, P1.1, R7.1, R9.1, U3.4
/AREF: C1.1, P1.2, U7.20
/Interface/5V0: C7.1, C8.1, C9.1, C10.1, C11.1, C14.1, C16.1, C28.1, D3.2, J1.1, L1.2, P1.3, P4.2, P7.1, P9.1, P10.1, P11.1, P34.1, R1.1, R2.1, R3.1, R4.2, R5.1, R6.1, R7.2, R8.1, R11.1, SP1.1, SW2.2, SW3.2, U1.1, U1.8, U1.14, U2.4, U5.2, U7.4, U7.6, U7.18
/Interface/12V: C5.1, C6.1, C17.1, C27.1, D4.2, J1.3, J2.3, P11.3, P17.2, P34.3, R13.1, U2.7, U3.7
/Interface/+Vlv: C13.1, D1.2, P11.2, P14.2
/Interface/+Vlv2: C31.1, D9.2, P34.2, P38.2
/Interface/-Vlv: D1.1, P14.1, Q1.2
/Interface/-Vlv2: D9.1, P38.1, Q3.2
/Interface/MISO: P4.1, P7.4, U1.2, U1.13, U7.16
/Interface/PC3_Pr1: P7.3, U7.26
/Interface/PD4_Valve2: Q1.1, R12.1, U7.2
/Interface/Pump: C29.1, P17.4, R5.2
/Interface/Pump_Ret: C29.2, P17.1, Q2.2
/Interface/SCK: P4.3, P7.5, R10.1, U1.3, U1.12, U7.17
/Interface/SCL: P9.2, P10.2, R3.2, U5.16, U7.28
/Interface/SDA: P9.3, P10.3, R2.2, U5.15, U7.27
/Interface/Spk: D3.1, Q4.2, R6.2, SP1.2
/Interface/~MOSI: P4.4, P7.8, U1.5, U1.10, U7.15
/Interface/~PB1_Pump: Q2.1, R16.2, U7.13
/Interface/~PD5_Valve: Q3.1, R14.1, U7.9
/Interface/~PD6_Spk: Q4.1, R15.2, U7.10
/Interface/~SS: P7.6, U1.4, U1.11, U7.14
/PB0: B12.1, U7.12
/PB6: C2.1, U7.7, X1.1
/PB7: C3.1, U7.8, X1.2
/PC0: B8.1, U7.23
/PC1: B9.1, U7.24
/PC2: B7.1, U7.25
/PC6: B10.1, U7.19
/PC7: B11.1, U7.22
/PD2: R21.1, SW2.1, U7.32
/PD7: B4.1, U7.11
/RESET: C4.1, C19.1, P4.5, R1.2, SW1.2, U7.29
/RXD: P5.4, U7.30
/TXD: P5.5, U7.31
/pwr/CB3: C15.2, U3.1
/pwr/CB5: C12.2, U2.1
/pwr/PWR_IN: D4.1, P13.1, P24.1
/pwr/VSW3: C15.1, D10.2, L2.1, U3.8
/pwr/VSW5: C12.1, D2.2, L1.1, U2.8
/rtc/32k: B3.1, U5.1
/rtc/BAT: BT1.+, C23.1, U5.14
/rtc/RST: B2.1, U5.4
/rtc/SQR: B1.1, R11.2, U5.3
/~PD3: R22.1, SW3.1, U7.1
/~RTS: C4.2, P5.6
GND: BT1.-, C1.2, C2.2, C3.2, C5.2, C6.2, C7.2, C8.2, C9.2, C10.2, C11.2, C13.2, C14.2, C16.2, C17.2, C18.2, C19.2, C23.2, C27.2, C28.2, C31.2, D2.1, D5.2, D6.2, D7.2, D8.2, D10.1, J1.2, J2.2, P4.6, P5.1, P5.2, P7.2, P9.4, P10.4, P13.2, P24.2, P24.3, Q1.3, Q2.3, Q3.3, Q4.3, R4.1, R12.2, R14.2, R15.1, R16.1, R21.2, R22.2, REF1.1, REF2.1, REF3.1, REF4.1, REF5.1, REF6.1, REF7.1, REF8.1, REF9.1, REF10.1, REF11.1, REF12.1, REF13.1, REF14.1, REF15.1, REF16.1, REF17.1, REF18.1, REF19.1, REF20.1, REF21.1, REF22.1, REF23.1, REF24.1, REF25.1, REF26.1, REF27.1, REF28.1, REF29.1, REF30.1, REF31.1, REF32.1, REF33.1, REF34.1, REF35.1, REF36.1, REF37.1, REF38.1, REF39.1, REF40.1, REF41.1, REF42.1, REF43.1, REF44.1, REF45.1, REF46.1, REF47.1, REF48.1, REF49.1, REF50.1, REF51.1, REF52.1, REF53.1, REF54.1, REF55.1, REF56.1, REF57.1, REF58.1, REF59.1, REF60.1, REF61.1, REF62.1, SW1.1, U1.7, U2.2, U2.3, U2.6, U3.2, U3.3, U3.6, U5.5, U5.6, U5.7, U5.8, U5.9, U5.10, U5.11, U5.12, U5.13, U7.3, U7.5, U7.21, W1.2, W2.2, X1.3
unnamed: D5.1, R8.2
unnamed: D6.1, R9.2
unnamed: D7.1, R10.2
unnamed: D8.1, R13.2
unnamed: U2.5, W1.1
unnamed: U3.5, W2.1

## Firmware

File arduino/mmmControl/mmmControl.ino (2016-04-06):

#include "uControl.h"
#include <Wire.h>
#include <SoftwareSerial.h>
#include <SPI.h>


#define SENSIRION_ADDR 64
#define FLOW_METER_ADDR SENSIRION_ADDR
#define SENSIRION_SCALE_FACTOR_F 140
#define SENSIRION_OFFSET_F 32000

/*
 * Flush and discard all serial input
 */
void Serial_flush_input(){
  while(Serial.available()){
    Serial.read();
  }
}

/*
 * compute check sum, send data
 * 
 * dat -- pointer to message data
 *   n -- number of message bytes (not including check sum)
 */
void send_msg(byte *dat, byte n){
  byte cksum = 0;
  for(byte i=0; i < n; i++){
    cksum += dat[i];
  }
  Serial.write(dat, n);
  Serial.write(cksum);
}

/*
 * stop exectution until next reset
 */
void error(byte error_code){
  while(1){
    for(int ii=0; ii < 10; ii++){
      Serial.print("ERROR:");// TODO: FORMAT ERROR STATUS PACKET
      Serial.println(error_code, DEC);
      for(byte i=0; i < error_code; i++){
	digitalWrite(LED, HIGH);
	delay(200);
	digitalWrite(LED, LOW);
	delay(200);
      }
      delay(600);
    }
  }
}
/*
 * Pump at given rate for duration in miliseconds.
 * rate = 0: off
 */
void control_pump(int rate){
  if(rate > 0){
    digitalWrite(PUMP_PIN, HIGH);
  }
  else{
    digitalWrite(PUMP_PIN, LOW);
  }
}
void pump_on(){
  control_pump(1);
}
void pump_off(){
  control_pump(0);
}

/*
 * Open valve
 * full closed 0 <= dc <= 1(full open)
 * State for two valves is set in bits 0,1
 * enable is bit 7. If bit 7 is set, control both valves
 */
void control_valve(int  state){
  if (!state &0x80) return;
  if((state & 0x01) == VALVE_OPEN){
    valve_is_closed = false;
    pressure_start = -1;
    digitalWrite(VALVE1_PIN, LOW);
  }
  else{
    valve_is_closed = true;
    pressure_start = millis();
    digitalWrite(VALVE1_PIN, HIGH);
  }
  if(((state & 0x02)>>1) == VALVE_OPEN){
    pressure_start = -1;
    digitalWrite(VALVE2_PIN, LOW);
  }
  else{
    pressure_start = millis();
    digitalWrite(VALVE2_PIN, HIGH);
  }
}
void valves_close(){
  control_valve(0x80);
}
void valves_open(){
  control_valve(0x83);
}

/*
 * Start sampling pressure sensor at given rate (20 Hz max)
 */
bool set_next_sample(unsigned long now_ms){
  unsigned int current = millis();
  next_sample_ms = now_ms + interval_ms;
  if(next_sample_ms < current){
    next_sample_ms = current + interval_ms;
  }
  if(next_sample_ms < now_ms){
    // millis() rollover!!! Should never have to worry.  Pi should reset between runs.
    // taked 49 days to roll over
    error(ROLLOVER_ERROR);
  }
}
boolean set_next_sample(){
  set_next_sample(next_sample_ms);
}
/*
 * Set next sample time for low rate data amb temp and pressure sensor
 */
bool lr_set_next_sample(unsigned long now_ms){
  unsigned int current = millis();
  lr_next_sample_ms = now_ms + lr_interval_ms;
  if(lr_next_sample_ms < current){
    lr_next_sample_ms = current + lr_interval_ms;
  }
  if(lr_next_sample_ms < now_ms){
    // millis() rollover!!! Should never have to worry.  Pi should reset between runs.
    // taked 49 days to roll over
    error(ROLLOVER_ERROR);
  }
}

void start_sampling(unsigned long __interval_ms){
  unsigned long now_ms = millis();
  if(__interval_ms != interval_ms){
    
    // Serial << "Start sampling" << __interval_ms << "\n";
    interval_ms = __interval_ms;
    if(__interval_ms > 0){

      sampling = true;
      set_next_sample(now_ms);
      lr_set_next_sample(now_ms);
    }
    else{
      sampling = false;
    }
  }
}

void read_cuff(byte *where){
  digitalWrite(SS, LOW);
  SPI.transfer(255);
  where[1] = SPI.transfer(255);
  where[0] = SPI.transfer(255);
  digitalWrite(SS, HIGH);
}

void read_amb_temp(byte *where){
#ifdef TEMP_STS21
  Wire.requestFrom(STS_ADDR, (byte)3);
  if(Wire.available() > 2){
    where[1] = Wire.read();
    where[0] = Wire.read();
  }
#else
    where[1] = 0;
    where[0] = 20; //20 c room temp?
#endif
}

void read_amb_pressure(byte *where){
#ifdef AMB_PRESSURE
  Wire.requestFrom(AMB_PRESS_ADDR, (byte)2);
  if(Wire.available() == 2){
    where[1] = Wire.read();
    where[0] =  Wire.read();
  }
#else
  where [1] = 0;
  where [0] = 0;
#endif
}

void read_flow(byte *where){
  byte n_flow;
  short flow;
  
  Wire.requestFrom(FLOW_METER_ADDR, 2);
  if(Wire.available() == 2){
    /* count = Wire.read()<<8; */ // this works
    /* count |= Wire.read(); */
    /* return (count - SENSIRION_OFFSET_F) / float(SENSIRION_SCALE_FACTOR_F); */
    where[1] = Wire.read(); // works!
    where[0] = Wire.read(); // works!
  }
}

void read_pulse(byte *where){
  cli();
  *(unsigned short*)where = analogRead(PULSE_PIN);
  sei();
}

void take_sample(){
  /*
    hirate data format
	  /*
	    byte#    purpose
	    0 -- MEASUREMENTS_PID
	    1 -- MILLISECS 0
	    2 -- MILLISECS 1
	    3 -- MILLISECS 2
	    4 -- MILLISECS 3
	    5 -- CUFF 0
	    6 -- CUFF 1
	    7 -- FLOW 0
	    8 -- FLOW 1
            9 -- PULSE 0
           10 -- PULSE 1
  */
  unsigned short *pulse_sensor = (unsigned short*)(hirate_data + 9);
  unsigned long now_ms = millis();
  if(sampling && (next_sample_ms <= now_ms)){
    set_next_sample();
    hirate_data[0] = MEASUREMENTS_PID;
    
    *(unsigned long *)(hirate_data + 1) = now_ms;
    
    // read pressure
    read_cuff(hirate_data + 5);
    
    // read flow
    read_flow(hirate_data + 7);

    // read pulse sensor
    read_pulse(hirate_data + 9);
    
    // send of hirate data
    send_msg(hirate_data, MEASUREMENTS_LEN);
  }
#ifdef NOT_DEFINED
  // not taking hirate samples can we take a low rate sample?
  if(valve_is_closed && sampling && 
     (lr_next_sample_ms <= now_ms) && // is it time for next lorate sample?
     (next_sample_ms  + 1 > now_ms)){ // 1 ms margin for low pri low rate data
    lr_set_next_sample(now_ms + lr_interval_ms);

    lorate_data[0] = LORATE_MEASUREMENTS_PID;
    *(unsigned long *)(lorate_data + 1) = now_ms;
    read_amb_pressure(lorate_data + 5);
    read_amb_temp(lorate_data + 7);
    send_msg(lorate_data, LORATE_MEASUREMENTS_LEN);
  }
#endif
}

/*
 * read serial stream into command buffer.  
 * return true if valid command is sent
 */

boolean serial_interact(){
  byte pos = 0;
  byte cksum = 0;
  boolean out = false;
  byte n_try = 0;

  if(Serial.available()){
    while(Serial.available() < COMMAND_LENGTH && n_try++ < 10){
      delay(1);
    }
    // delayMicroseconds(500); // wait for rest of message (BUG ALERT!!!)
    // take_sample();

    if(Serial.available() >= COMMAND_LENGTH){
      if(COMMAND_START == Serial.read() && COMMAND_START == Serial.read()){
	out = true; // new data
	for(byte ii=2; ii < COMMAND_LENGTH; ii++){
	  char c = Serial.read();
	  command[pos] = c;
	  if(pos != 0){
	    cksum += command[pos];
	    cksum %= 256;
	    /* 
	       Serial.print(command[pos], DEC);
	       Serial.print(":");
	       Serial.print(cksum, DEC);
	       Serial.print(",");
	    */
	  }
	  else{
	    /*
	      Serial.print(command[pos], DEC);
	      Serial.print("!!");
	    */
	  }
	  pos++;
	}
	if((byte)command[0] == (byte)cksum){ 
	  //  new data is valid
	  /*
	    byte#    purpose
	    0 -- 0x7F COMMAND_START
	    1 -- 0x7F COMMAND_START
	    2 -- checksum
	    3 -- initialize
	    4 -- sample interval
	    5 -- pump control
	    6 -- valve control
	    7 -- status request
	    8 -- \n COMMAND_END
	  */
	  if(command[1] == 1){ // Initialzation Command
	    bpc_setup();
	    command[1] = 2; // Set to initialized
	  }
	  start_sampling(SAMPLE_INTERVAL_STEP_MS * command[2]); // Sampling interval
	  // // Echo sample interval?
	  // short_msg[1] = 'S';
	  // short_msg[2] = interval_ms;
	  // send_msg(short_msg, 3);
	
	  control_pump((int)command[3]);
	  control_valve((int)command[4]);
	
	  if(command[5]){ // status
	    if((command[5] >> 0) & 1){
	      // CUFF
	      status_msg[3] = 0;
	      *(unsigned short*)(status_msg + 1) = *(unsigned short*)(hirate_data + 5);
	      send_msg(status_msg, 4);
	    }
	    if((command[5] >> 1) & 1){
	      // FLOW
	      status_msg[3] = 1;
	      *(unsigned short*)(status_msg + 1) = *(unsigned short*)(hirate_data + 7);
	      send_msg(status_msg, 4);
	    }
	    if((command[5] >> 2) & 1){
	      // PULSE
	      status_msg[3] = 2;
	      *(unsigned short*)(status_msg + 1) = *(unsigned short*)(hirate_data + 9);
	      send_msg(status_msg, 4);
	    }
	    if((command[5] >> 3) & 1){
	      // AMB PRESSURE
	      status_msg[3] = 3;
	      read_amb_pressure(status_msg + 1);
	      send_msg(status_msg, 4);
	    }
	    if((command[5] >> 4) & 1){
	      // AMB TEMP
	      status_msg[3] = 4;
	      read_amb_temp(status_msg + 1);
	      send_msg(status_msg, 4);
	    }
	    if((command[5] >> 5) & 1){
	      // PUMP
	      status_msg[3] = 5;
	      status_msg[1] = *pump_state_p;
	      status_msg[2] = 0;
	      send_msg(status_msg, 4);
	    }
	    if((command[5] >> 6) & 1){
	      // VALVE
	      status_msg[3] = 6;
	      status_msg[1] = (*valve_state_p)&0x7f;
	      status_msg[2] = 0;
	      send_msg(status_msg, 4);
	    }
	    if((command[5] >> 7) & 1){
	      // sample interval ms
	      status_msg[3] = 7;
	      status_msg[1] = interval_ms;
	      status_msg[2] = 0;
	      send_msg(status_msg, 4);
	    }
	  }
	}
	else{ // got new data but cksum was wrong
	  short_msg[1] = 'C'; // command 
	  short_msg[2] = 'C'; // check sum
	  send_msg(short_msg, 3);
	  Serial_flush_input();
	}
      }
      else{ // got new data but start of command was wrong
	short_msg[1] = 'C'; // command
	short_msg[2] = 'S'; // start
	send_msg(short_msg, 3);
	Serial_flush_input();
      }
    }
    else{
      short_msg[1] = 'C'; // command 
      short_msg[2] = 'L'; // length
      send_msg(short_msg, 3);
      short_msg[1] = 'C'; // command 
      short_msg[2] = Serial.available();
      send_msg(short_msg, 3);
      while(Serial.available()){
	Serial.read();
      }
      Serial_flush_input();
    }
  }
  return out;
}

void bpc_setup(){
  // configure pins
  Flow_cursor=0;
  Flow_last_end = 0;
  
  pinMode(PUMP_PIN, OUTPUT);
  pinMode(VALVE1_PIN, OUTPUT);
  pinMode(VALVE2_PIN, OUTPUT);
  // open valve as audio feed back
  valves_open();
  
  // turn off pump
  pump_off();

#ifdef SERIAL_FLOW_SENSOR
// start flow sensor serial
  Flow_serial.begin(19200);

  // stop readings
  if(!Flow_run_command("s\r\n", FLOW_MAX_TRY)){
    short_msg[1] = 'F';
    short_msg[2] = 's';
    send_msg(short_msg, 3);    
  }
    
  // get flow readings
  if(!Flow_run_command("mod=f\r\n", FLOW_MAX_TRY)){
    short_msg[1] = 'F';
    short_msg[2] = 'm';
    send_msg(short_msg, 3);    
  } 
  //  set resolution, res=4==> 12.5 Hz res=5 ==> rate=6.25 Hz res=7 ==> rate ~1.56 Hz
  if(!Flow_run_command("res=5\r\n", FLOW_MAX_TRY)){
    short_msg[1] = 'F';
    short_msg[2] = 'r';
    send_msg(short_msg, 3);    
  } 
  // start measurements
  if(!Flow_run_command("go\r\n", FLOW_MAX_TRY)){
    short_msg[1] = 'F';
    short_msg[2] = 'g';
    send_msg(short_msg, 3);    
  } 
#endif
  // Serial.println("bpc_setup() flow ready");
  // start I2C
  Wire.begin();
  Wire.beginTransmission(SENSIRION_ADDR);
  Wire.write(0x10);
  Wire.write(0x00);
  Wire.endTransmission();
  valves_close();
 #ifdef TEMPSTS21 
  // start STS21 temperature sensor
  Wire.beginTransmission(STS_ADDR);
  Wire.write(STS_HOLD_MASTER); // option: STS_NOHOLD_MASTER
  Wire.endTransmission();
#endif
  // start SPI for gage pressure
  SPI.begin();
  SPI.setDataMode(SPI_MODE0);
  SPI.setClockDivider(SPI_CLOCK_DIV32); //  or 2,4,8,16,32,64,128
 
  // start sampling at max rate
  start_sampling(SAMPLE_INTERVAL_STEP_MS);
}
void Flow_convert();
int Flow_read();
void setup(){
  // open serial stream
  Serial.begin(BAUDRATE);
  // Serial.println("uControl");
  bpc_setup();
  // toggle valve
  // Serial.println("ready");
  short_msg[1] = 'R'; // code for ready
  short_msg[2] = '!';
  send_msg(short_msg, 3);
}
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

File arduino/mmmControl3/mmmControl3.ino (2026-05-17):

/*
 * mmMControl3.ino
 * Based on mmMControl2 — adds analog PWM pump control.
 * 
 * Change from mmMControl2:
 *   control_pump() now uses analogWrite(PUMP_PIN, rate) so that
 *   command[3] (0-255) sets pump speed, not just on/off.
 *   Pin 9 (PUMP_PIN) supports hardware PWM on ATmega328P (Timer 1).
 *   All other behaviour is identical to mmMControl2.
 */

#include "uControl.h"
#include <Wire.h>
#include <SoftwareSerial.h>
#include <SPI.h>

#define SENSIRION_ADDR_1 64
#define SENSIRION_ADDR_2 1
#define HONEYWELL_ADDR 0x49

void Serial_flush_input(){
  while(Serial.available()){
    Serial.read();
  }
}

void send_msg(byte *dat, byte n){
  byte cksum = 0;
  for(byte i=0; i < n; i++){
    cksum += dat[i];
  }
  Serial.write(dat, n);
  Serial.write(cksum);
}

void error(byte error_code){
  while(1){
    for(int ii=0; ii < 10; ii++){
      Serial.print("ERROR:");
      Serial.println(error_code, DEC);
      for(byte i=0; i < error_code; i++){
        digitalWrite(LED, HIGH);
        delay(200);
        digitalWrite(LED, LOW);
        delay(200);
      }
      delay(600);
    }
  }
}

/*
 * Pump at given rate 0-255.
 * 0   = off
 * 1-255 = analogWrite PWM duty cycle (pin 9 = Timer1, hardware PWM)
 * 
 * This replaces the boolean digitalWrite from mmMControl2.
 */
void control_pump(int rate){
  if(rate <= 0){
    analogWrite(PUMP_PIN, 0);
    digitalWrite(PUMP_PIN, LOW);   // ensure fully off
  }
  else{
    analogWrite(PUMP_PIN, constrain(rate, 1, 255));
  }
}

void pump_on(){
  control_pump(255);
}
void pump_off(){
  control_pump(0);
}

void control_valve(int state){
  // Bit 7 (0x80) is the "enable" bit. If not set, ignore this command
  // and leave valves in their current state. Note: original code was
  //     if (!state & 0x80) return;
  // which due to C precedence parses as  (!state) & 0x80,  always 0,
  // so the early-return never fired and a state=0 command would still
  // command both valves CLOSED. Parentheses make the intent explicit.
  if (!(state & 0x80)) return;
  if((state & 0x01) == VALVE_OPEN){
    valve_is_closed = false;
    pressure_start = -1;
    digitalWrite(VALVE1_PIN, LOW);
  }
  else{
    valve_is_closed = true;
    pressure_start = millis();
    digitalWrite(VALVE1_PIN, HIGH);
  }
  if(((state & 0x02)>>1) == VALVE_OPEN){
    pressure_start = -1;
    digitalWrite(VALVE2_PIN, LOW);
  }
  else{
    pressure_start = millis();
    digitalWrite(VALVE2_PIN, HIGH);
  }
}
void valves_close(){
  control_valve(0x80);
}
void valves_open(){
  control_valve(0x83);
}

bool set_next_sample(unsigned long now_ms){
  unsigned int current = millis();
  next_sample_ms = now_ms + interval_ms;
  if(next_sample_ms < current){
    next_sample_ms = current + interval_ms;
  }
  if(next_sample_ms < now_ms){
    error(ROLLOVER_ERROR);
  }
}
boolean set_next_sample(){
  set_next_sample(next_sample_ms);
}
bool lr_set_next_sample(unsigned long now_ms){
  unsigned int current = millis();
  lr_next_sample_ms = now_ms + lr_interval_ms;
  if(lr_next_sample_ms < current){
    lr_next_sample_ms = current + lr_interval_ms;
  }
  if(lr_next_sample_ms < now_ms){
    error(ROLLOVER_ERROR);
  }
}
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

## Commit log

2015-07-06 old files from uC_v3 imported
    [BBB.sch, FlyingBone-Back.gbl, FlyingBone-Front.gtl, FlyingBone-Mask_Back.gbs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]
2015-07-09 uCm initial commit, work in progress
    [BBB.sch, uControl_pwr.sch, uControl_rtc.sch]
2015-07-12 uCm work in progress
    [BBB.sch, interface.sch, uCm.sch, uCm_pwr.sch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]
2015-07-12 made standard directory structure
    [BBB.sch, FlyingBone-Back.gbl, FlyingBone-Front.gtl, FlyingBone-Mask_Back.gbs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]
2015-07-12 uCm KISS version
    [interface.sch, uCm.sch, uCm_pwr.sch, uCm_rtc.sch]
2015-08-24 work in progress
    [interface.sch, uCm.kicad_pcb, uCm.sch, uCm_BoM_sch.csv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]
2015-09-01 making some progress on the PCB
    [BBB.sch, FlyingBone-Back.gbl, FlyingBone-Front.gtl, FlyingBone-Mask_Back.gbs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]
2015-09-02 layout, work in progress
    [uCm.kicad_pcb]
2015-09-05 Board layout complete. Gerbers, PDF', BoM generated.
    [uCm-B_Cu.gbl, uCm-B_Mask.gbs, uCm-B_SilkS.gbo, uCm-Edge_Cuts.gm1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]
2015-12-06 changed power supply section
    [FlyingBone-Back.gbl, FlyingBone-Front.gtl, FlyingBone-Mask_Back.gbs, FlyingBone-Mask_Front.gts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]
2015-12-07 power supply sections changed
    [uCm.kicad_pcb, uCm.xlsx, uCm_BoM_sch.csv, uCm_pwr.sch]
2015-12-07 layout finalized, needs a check for errors
    [interface.sch, uCm-B.Cu.gbl, uCm-B.Mask.gbs, uCm-B.Paste.gbp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]
2015-12-08 some mods to PCB layout
    [uCm-B.Cu.gbl, uCm-B_Cu.gbl, uCm-B_Mask.gbs, uCm-B_Paste.gbp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]
2015-12-08 renamed uCm to mmM
    [BBB.sch, interface.sch, mmM-B.Cu.gbl, mmM-B.Mask.gbs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]
2015-12-08 Fresh BOM for mmM
    [interface.sch, mmM.kicad_pcb, mmM.sch, mmM_BOM_pcb.csv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]
2015-12-09 added pull down resistors on microcontroller outputs
    [interface.sch, mmM-B.Cu.gbl, mmM-B.Mask.gbs, mmM-B.Paste.gbp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]
2015-12-09 mods to board layout
    [interface.sch, mmM-B.Cu.gbl, mmM-B.Mask.gbs, mmM-B.Paste.gbp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]
2015-12-10 PCB optimization
    [interface.sch, mmM-B.Cu.gbl, mmM-B.Mask.gbs, mmM-B.Paste.gbp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]
2015-12-17 BoM and 3D render work in progress
    [C0603.step, C_2225.step, C_2917.step, DO-214AB_SMC.step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]
2015-12-17 3D render work in progress
    [C0603.step, C_2225.step, C_2917.step, DO-214AB_SMC.step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]
2015-12-19 trying to fix my mess
    [C0603.step, C_2917.step, DO-214AB_SMC.step, DO-214AC_SMA.step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]
2015-12-19 fresh 3D renders
    [mmM.kicad_pcb]
2015-12-27 added Cap across RST sw. Fresh Gerbers, PDF. Final v1 ready for prototype
    [interface.sch, mmM-B.Cu.gbl, mmM-B.Mask.gbs, mmM-B.Paste.gbp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]
2015-12-27 made a pretty schematic, fresh symbols
    [interface.sch, mmM.sch, pwr.sch, rtc.sch]
2015-12-29 new BoM format for seeed
    [mmM_BoM_seeed.xls, mmM_BoM_seeed_new.csv, mmM_BoM_seeed_new.xls]
2016-02-13 new pumpt mount
    [pump_mount.scad]
2016-02-13 pump_clamp update to get rid of overhang
    [pump_mount.scad]
2016-02-14 increase diameters by.5mm
    [pump_mount.scad]
2016-02-14 added reference from okenseiko
    [pump_mount.scad]
2016-02-15 Board test program initial commit
2016-02-16 schematic label errors corrected, Git issue #2
    [interface.sch, mmM.CSV, mmM.GBL, mmM.GBO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]
2016-02-17 mmM enclosure WIP
    [pump_mount.step, pump_mount.stl]
2016-02-20 add TI voltage translator datasheet
2016-02-20 add gauge pressure sensor test
2016-02-23 updated pump height above board in p_clamp
    [pump_mount.scad]
2016-03-12 minor mod to pump_mount final creation
    [pump_mount.scad, pump_mount.stl]
2016-03-13 add second valve control
2016-03-13 correct Valve 2 pin mistake
2016-03-25 add beginnings of flowmeter input adapter
    [flowmeter.scad]
2016-04-01 added test code for Sensirion flow sensor
    [flowmeter.scad]
2016-04-06 integrated Sensirion flow meter
2016-05-01 usb panel mount outline for laser cutting
2016-05-02 added 3D printed enclosure frame
    [mmM_case.scad]
2016-05-07 added dxf file
    [mmM_case.dxf, mmM_case.scad]
2016-05-07 added screw holes and conntoured edges to bottom
    [mmM_case.dxf, mmM_case.scad]
2016-05-07 added 4100 flow meter spec
    [mmM_case.scad]
2016-05-07 mounting holes for all components in a separate file
2016-05-09 added openings to case, saved in svg file
    [mmM_case.scad]
2016-05-10 update flow sensor footprint
2016-05-13 tweak to case
    [mmM_case.scad]
2016-05-13 increased acr thickness
    [mmM_case.scad]
2016-07-16 copied util.py from arduino/mmmControl2
2016-07-16 first printed BP run success!
2016-07-31 fixed bug with valves. LEDs now correspond to mmM_control status packets.
2016-08-14 changed 'patient' to 'user'
2017-02-04 increased max pressure to 300 mmHG
2017-04-01 added code to support Honeywell flow sensor
2017-04-01 added support for honeywell flow meter
2017-04-01 ignore bad data from honeywell sensor
2017-04-02 add liquid pressure sensor support
2017-04-02 found bug in mmM control (liquid pressure) address
2017-04-02 add liquid pressure sensor datasheets
2017-04-02 adjusted number of taps to 1000 and brought low low pass cuttoff down to .1 Hz
2017-08-06 comment out debug code, and report proper counts from the flow sensor
2018-03-31 added honeywell flow sensor to drive.py
2020-02-22 add i2c pressure sensor data sheet
2020-02-24 Liquid pressure example, and HardWire library
2026-05-02 Migrate uControl suite to Python 3
    - Apply 2to3 conversions (print functions, dict items, xrange)
    - Fix packet alignment and synchronization logic in drive.py
    - Resolve numpy sum() TypeError by coercing byte slice to integer list
    - Fix ShortPID %x formatting TypeError with ord()
    - Update pickle.dump to use binary write mode ('wb')
2026-05-16 added pump rate commands.
2026-05-17 made change to keep valves open by default
2026-06-07 mmM update for kicad 10
    [interface-2026-05-21-19-06-37.sch, interface-2026-05-21-19-13-05.sch, interface.kicad_sch, mmM-2026-05-21-19-06-37.sch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]
2026-06-07 bard convert to ver 10
    [mmM.kicad_pcb]
